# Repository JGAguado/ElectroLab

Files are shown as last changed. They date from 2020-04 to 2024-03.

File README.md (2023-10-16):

[][documentation]
[][releases]
[](LICENSE)
[][elecrow]

[][maintenance]
[][buymecoffee]

# ElectroLab

The ElectroLab board is an electronic trainer designed for educational purposes. It should be considered as a beginner-friendly guided solution for learning practical electronics where no prior knowledge is required.

With its big set of integrated components, the ElectroLab offers a very powerful and versatile platform for building up your electronic circuits in very few steps.

<p float="left">
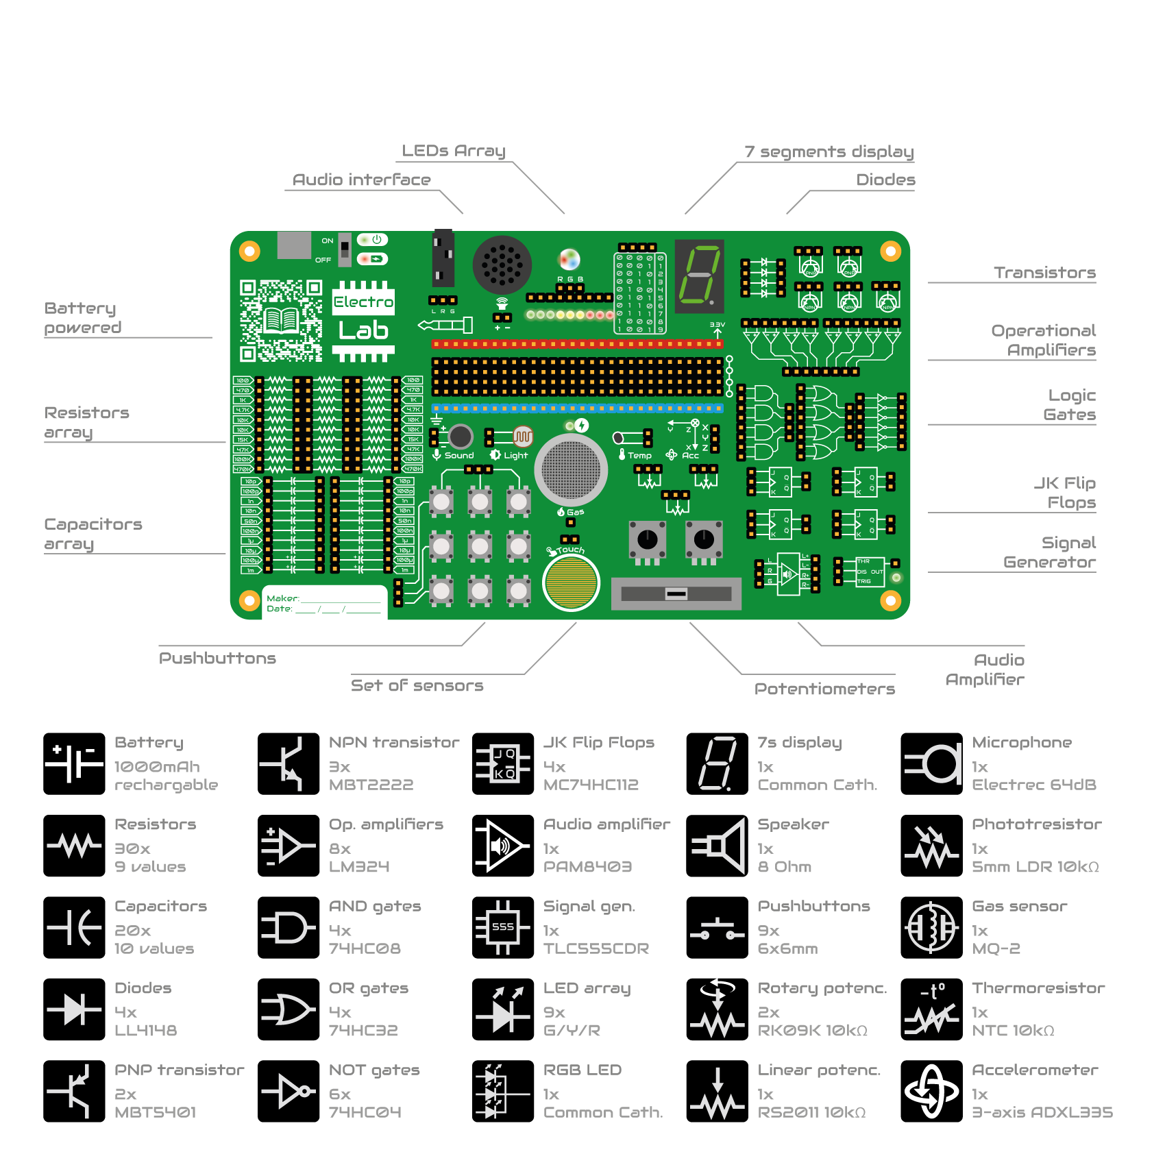
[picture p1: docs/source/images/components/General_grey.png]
   
</p>

[documentation-shield]: https://readthedocs.org/projects/electrolab/badge/?version=latest&style=for-the-badge
[documentation]: https://electrolab.readthedocs.io/en/v3/

[releases-shield]: https://img.shields.io/github/release/JGAguado/ElectroLab.svg?style=for-the-badge
[releases]: https://github.com/JGAguado/ElectroLab/releases

[license-shield]: https://img.shields.io/badge/License-CC%20BY--NC--SA%204.0-lightgrey.svg?style=for-the-badge

[maintenance-shield]: https://img.shields.io/badge/maintainer-J.%20G.%20Aguado-blue.svg?style=for-the-badge
[maintenance]: https://github.com/JGAguado

[buymecoffee-shield]: https://img.shields.io/badge/buy%20me%20a%20coffee-support-yellow.svg?style=for-the-badge
[buymecoffee]: https://www.buymeacoffee.com/J.G.Aguado

[buyit-shield]: https://img.shields.io/badge/get%20it%20on-elecrow-399BD7.svg?style=for-the-badge
[elecrow]: https://www.elecrow.com/electrolab.html

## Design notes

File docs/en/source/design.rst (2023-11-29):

📐 Design
=======================

.. _schematic:
Electronic schematics
---------------------
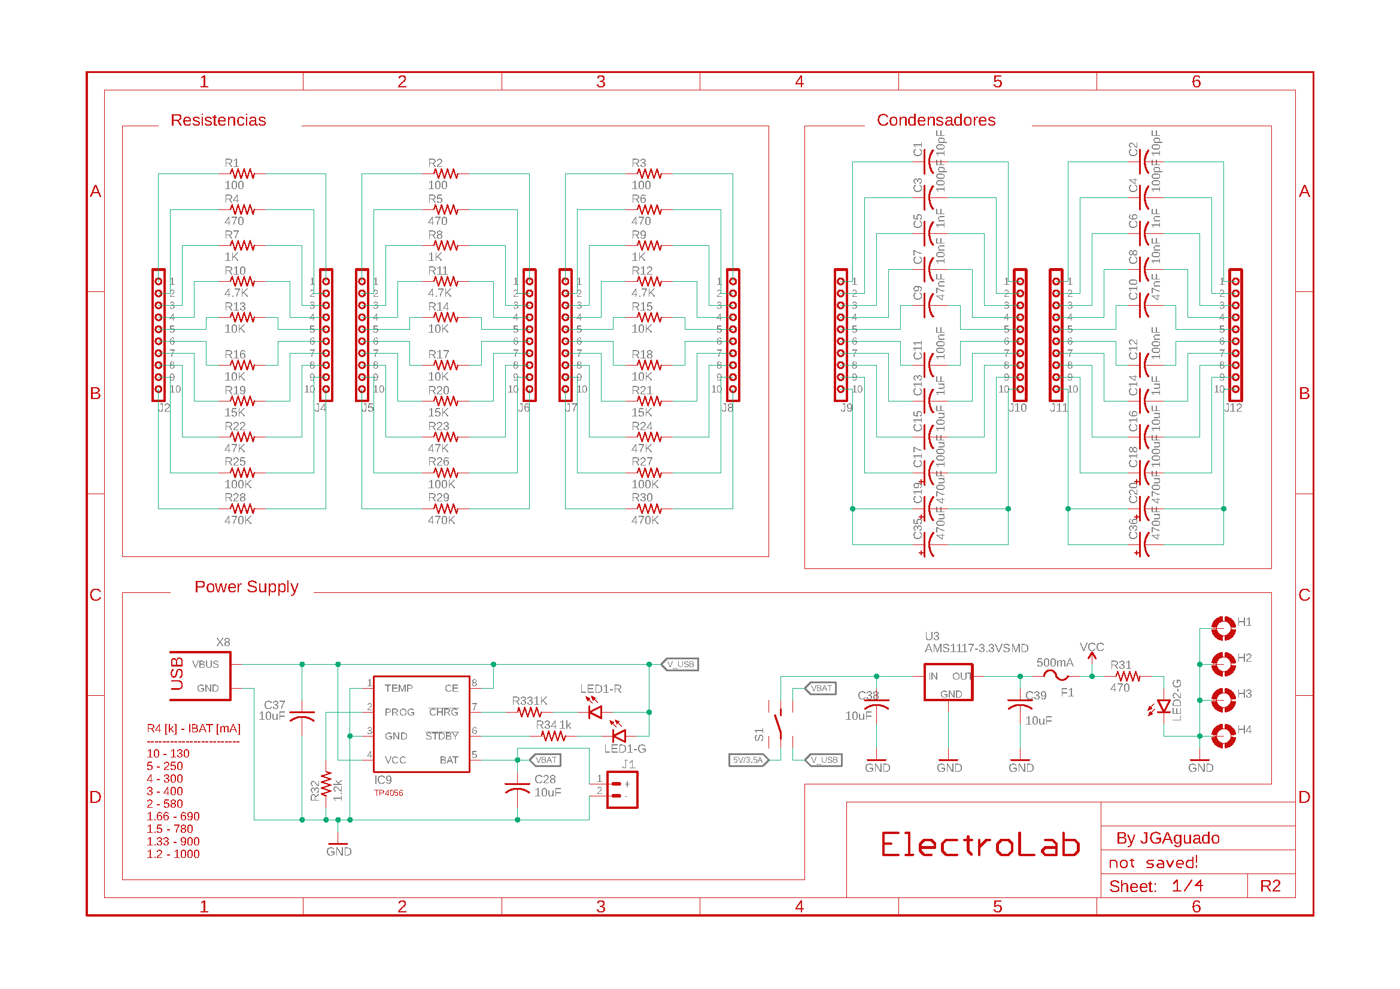
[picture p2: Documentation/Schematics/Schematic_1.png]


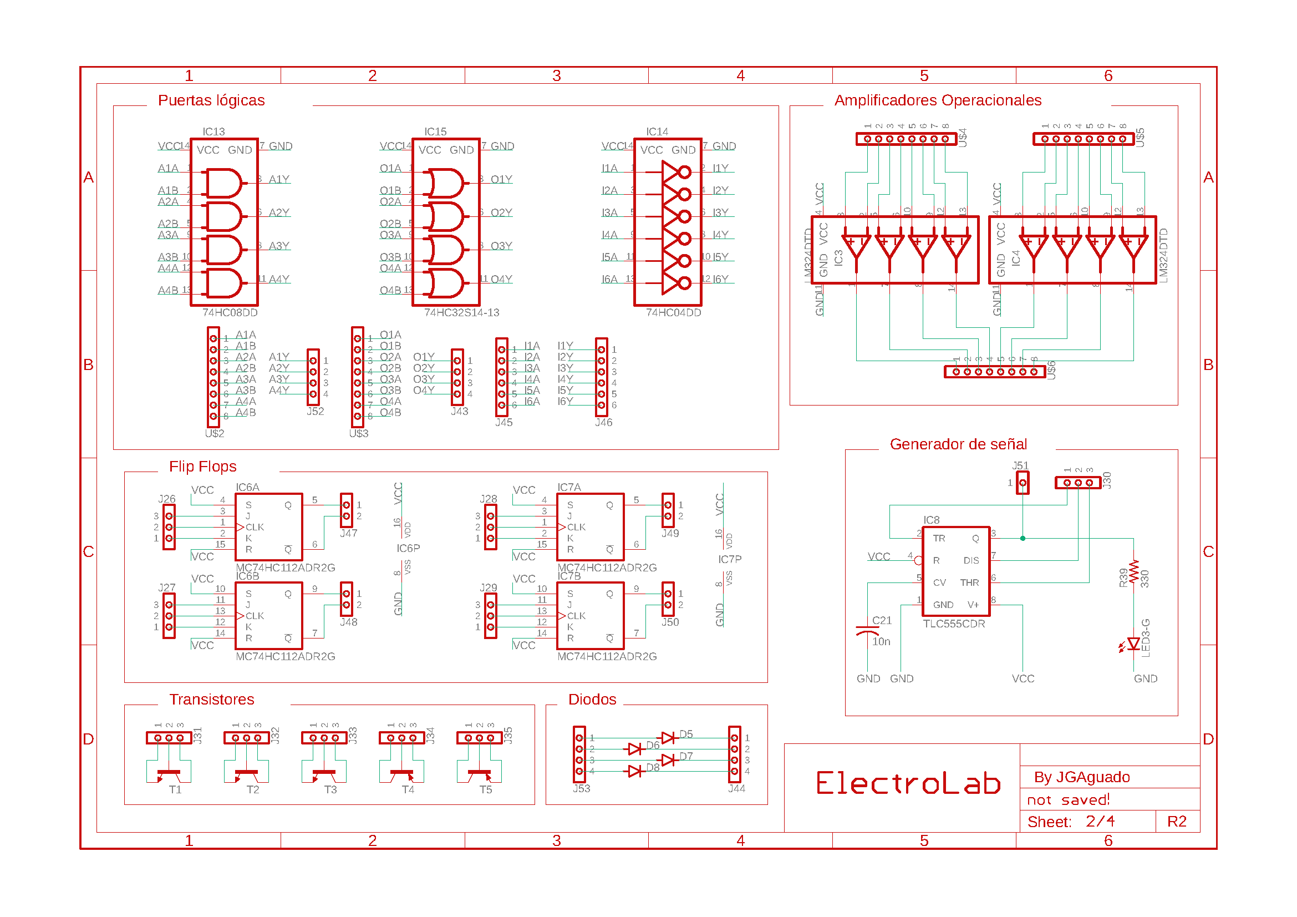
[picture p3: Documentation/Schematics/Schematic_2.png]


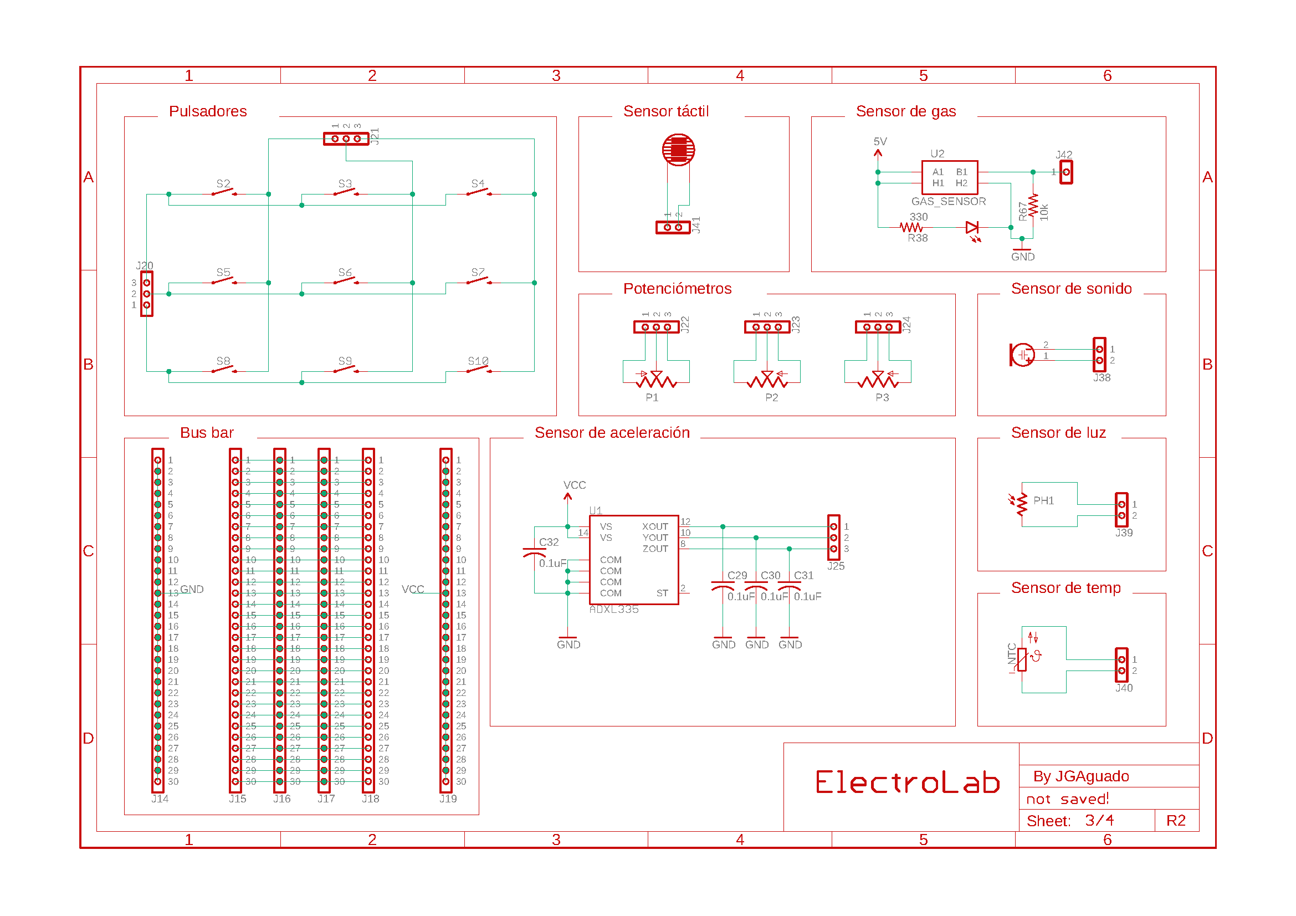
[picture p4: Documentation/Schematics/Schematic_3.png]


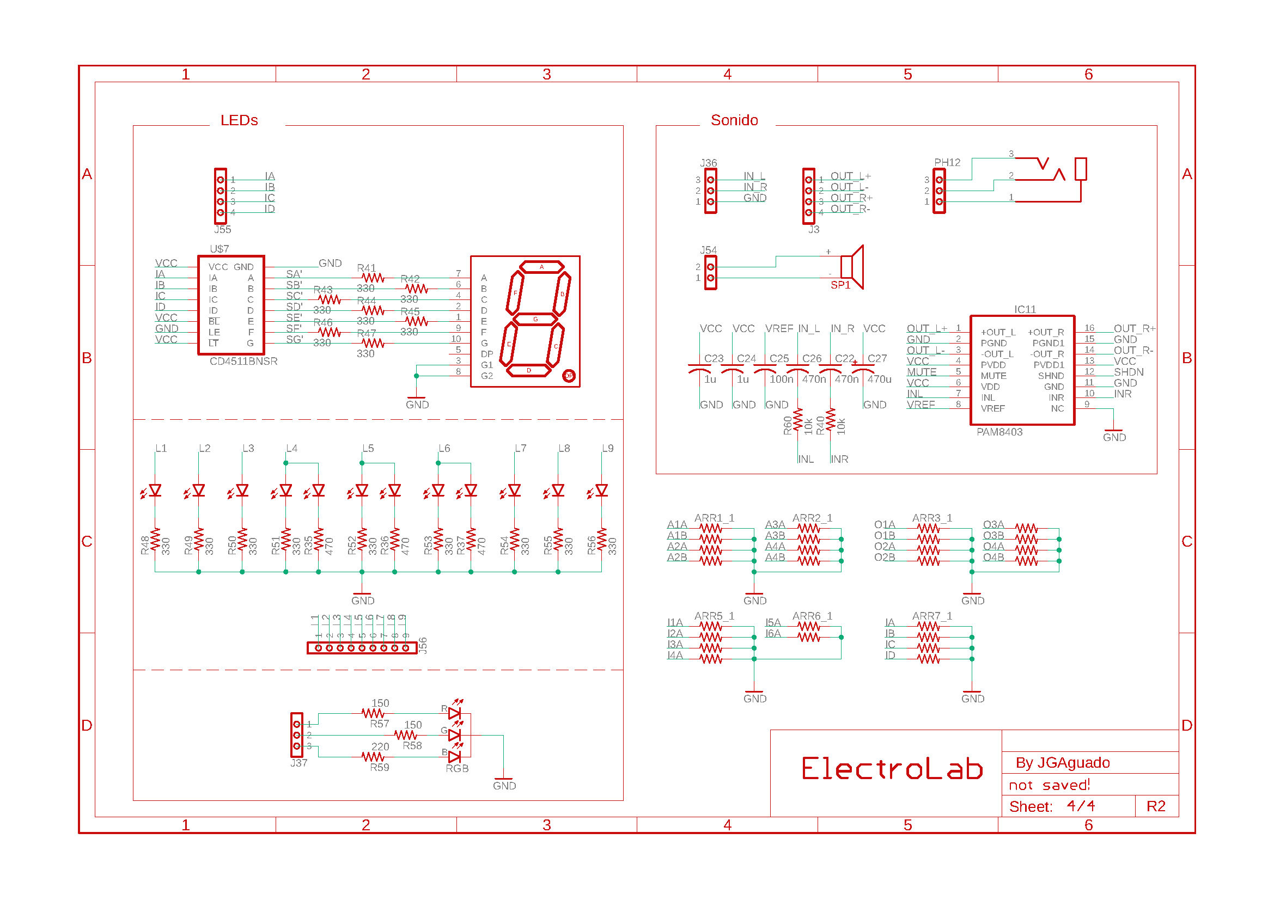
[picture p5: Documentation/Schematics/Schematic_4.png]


:download:`Download PDF <../../../Documentation/Schematics/Schematic.pdf>`

.. _pcb:

:term:`PCB`
----------

.. raw:: html

    <iframe src="_static/ibom.html" height="800px" width="100%"></iframe>

Technical Specifications
--------------------------

Electrical
^^^^^^^^^^^^

.. list-table:: 
    :widths: 50 20 20 20 20
    :header-rows: 1
    :stub-columns: 1

    * - Parameter
      - Symbol
      - Min.
      - Max.
      - Unit
    * - Supply voltage (USB)
      - :math:`V_{DC}`
      -  
      - 5
      - *V*
    * - Current consumption
      - 
      - 0.5 
      - 800
      - :math:`mA`

Environment
^^^^^^^^^^^^
.. list-table:: 
    :widths: 50 20 20 20 20 20
    :header-rows: 1
    :stub-columns: 1

    * - Parameter
      - Symbol
      - Min.
      - Typ.
      - Max.
      - Unit
    * - Working temperature [1]_
      - :math:`T_{amb}`
      - 0
      - 25 
      - 60
      - *°C*
    * - Storage temperature [1]_
      - :math:`T_{amb}`
      - 0
      - 25 
      - 60
      - *°C*

.. [1] Based on components datasheets.

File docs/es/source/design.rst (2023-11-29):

📐 Diseño
=======================

.. _schematic:
Esquemas electrónicos
---------------------








:download:`Download PDF <../../../Documentation/Schematics/Schematic.pdf>`

.. _pcb:

:term:`PCB` (Placa de Circuito Impreso)
----------

.. raw:: html

    <iframe src="_static/ibom.html" height="800px" width="100%"></iframe>

Especificaciones Técnicas
--------------------------

Eléctricas
^^^^^^^^^^^^

.. list-table:: 
    :widths: 50 20 20 20 20
    :header-rows: 1
    :stub-columns: 1

    * - Parámetro
      - Símbolo
      - Mín.
      - Máx.
      - Unidad
    * - Voltaje de alimentación (USB)
      - :math:`V_{DC}`
      -  
      - 5
      - *V*
    * - Consumo de corriente
      - 
      - 0.5 
      - 800
      - :math:`mA`

Ambientales
^^^^^^^^^^^^

.. list-table:: 
    :widths: 50 20 20 20 20 20
    :header-rows: 1
    :stub-columns: 1

    * - Parámetro
      - Símbolo
      - Mín.
      - Typ.
      - Máx.
      - Unidad
    * - Temperatura de trabajo [1]_
      - :math:`T_{amb}`
      - 0
      - 25 
      - 60
      - *°C*
    * - Temperatura de almacenamiento [1]_
      - :math:`T_{amb}`
      - 0
      - 25 
      - 60
      - *°C*

.. [1] Basado en las hojas de datos de los componentes.

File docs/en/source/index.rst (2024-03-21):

ElectroLab
###############

.. raw:: html
        
    <iframe src="_static/carousel.html" style="width: 100%; height: 300px; border: none;"></iframe>

Welcome to the documentation page of the |Product|, an electronic trainer designed for educational purposes.
It should be considered as a beginner-friendly guided solution for learning practical electronics
where no prior knowledge is required.

With its big set of integrated components, the ElectroLab offers a very powerful and versatile platform for building up your electronic circuits
in very few steps.

Contents
--------

:doc:`safety`
    How to operate and manipulate the |Product|.

:doc:`getting_started`
    First steps for starting with the |Product|.

:doc:`assembly`
    Get to know how to prepare your |Product|.

:doc:`examples`
    Example circuits ready to deploy on the |Product|.

:doc:`design`
    Design files of the |Product|.

.. _support:
Technical support
-----------------

If you have technical problems or cannot find the information that you need in the provided documentation, 
please contact me directly:

:Author: |Author|
:Contact: |Email|

:Board: |Product|
:Version: |Version|
:Date: |Date|

.. toctree::
   :maxdepth: 2
   :hidden:

   safety
   🛒 Buy <https://www.elecrow.com/electrolab.html>   
   getting_started
   assembly
   examples 
   components
   design   
   glossary
   faq

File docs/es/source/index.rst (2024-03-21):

ElectroLab
###############

.. raw:: html
        
    <iframe src="_static/carousel.html" style="width: 100%; height: 300px; border: none;"></iframe>

¡Bienvenido a la página de documentación de la |Product|!
Un intuitivo entrenador electrónico para principiantes y amantes de los circuitos.

Con su amplio conjunto de componentes integrados, la ElectroLab ofrece una plataforma muy potente y versátil para construir circuitos electrónicos
en muy pocos pasos.

Contenidos
--------

:doc:`safety`
    Cómo operar y manipular la |Product|.

:doc:`getting_started`
    Primeros pasos para comenzar con la |Product|.

:doc:`assembly`
    Aprende cómo montar tu |Product|.

:doc:`examples`
    Circuitos de ejemplo listos para implementar en |Product|.

:doc:`design`
    Archivos de diseño de la |Product|.

.. _support:
Soporte técnico
-----------------

Si tienes problemas técnicos o no puedes encontrar la información que necesitas en la documentación proporcionada, 
por favor contáctame directamente:

:Autor: |Author|
:Contacto: |Email|

:Placa: |Product|
:Versión: |Version|
:Fecha: |Date|

.. toctree::
   :maxdepth: 2
   :hidden:

   safety
   🛒 Comprar <https://www.elecrow.com/electrolab.html>      
   getting_started
   assembly
   examples 
   components
   design   
   glossary
   faq

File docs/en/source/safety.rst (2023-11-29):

🦺 Safety guidelines
=================

These safety guidelines, the operation instructions and the limit values listed in :doc:`specs` are to be read carefully before operating the product.

.. Caution::
    This product has been designed for educational applications. 
    It was not designed for any use involving serious risks or hazards that could lead to death, injury, serious physical damage, or loss of any kind without the implementation of exceptionally stringent safety precautions.

Before the operation
--------------------
Before working with the |Product|, make sure to meet all of the following criteria:

- The |Product| is placed in a stable non-conductive surface.
- There are no objects or debris stuck in between the male pins of the surface of the board.
- Do not manipulate the board if you have wet hands or in such conditions that could lead to a short-circuit.
- Do not manipulate the board if you feel that you are electrostatically charged.
- Some components have polarity, meaning that they need a specific way of being connected.Please pay attention to the (⚠️) indications in this document related to those components.

:term:`LiPo` battery powered
----------------------
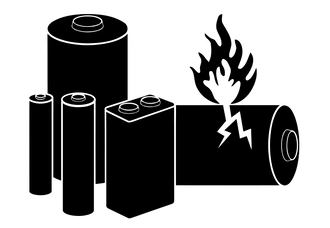
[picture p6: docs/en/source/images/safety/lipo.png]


Due to the high power density of :term:`LiPo` batteries, the |Product| is powered directly by a 1000mAh :term:`LiPo` battery. Therefore there are specific electronics embeded in charge of the battery 
management, including charge/discharge of the battery and protections against low-voltage levels and short-circuits. 

However it's not recommended to leave the product unatended while charging for long time. In case you observe a high increase of the device's temperature or you 
smell burn, immediatelly disconnect the device from the charging USB.

If you have any question, please check with :ref:`technical support <support>` before taking any action potentially dangerous.

Protection against :term:`ESD`
------------------------------

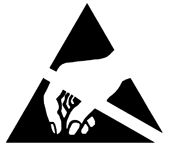
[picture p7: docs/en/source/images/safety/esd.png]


The |Product| contains components sensitive to :term:`ESD`, which can be damaged by inappropriate handling. 
It's therefore necessary to provide some safety precautions against :term:`ESD` during the handling and operation.

|
|

Usage, transport and storage
----------------------------

During the use, transport and storage, this product must be protected from any mechanical stress 
(forces applied over the board or it's components), temperatures out of the data-sheet's range, high 
environmental humidity or aggressive atmospheres.

Avoid using it in areas where it cannot be assured the previously mentioned environmental conditions.

Repairs
-------

If any of the components on the board gets damaged, a reparation is possible. This repair can be performed by 
yourself if you identify the problem and have the means for desoldering & soldering. If this is not the case,
just write to the :ref:`support <support>` mail to reach a solution.

Disposal
--------

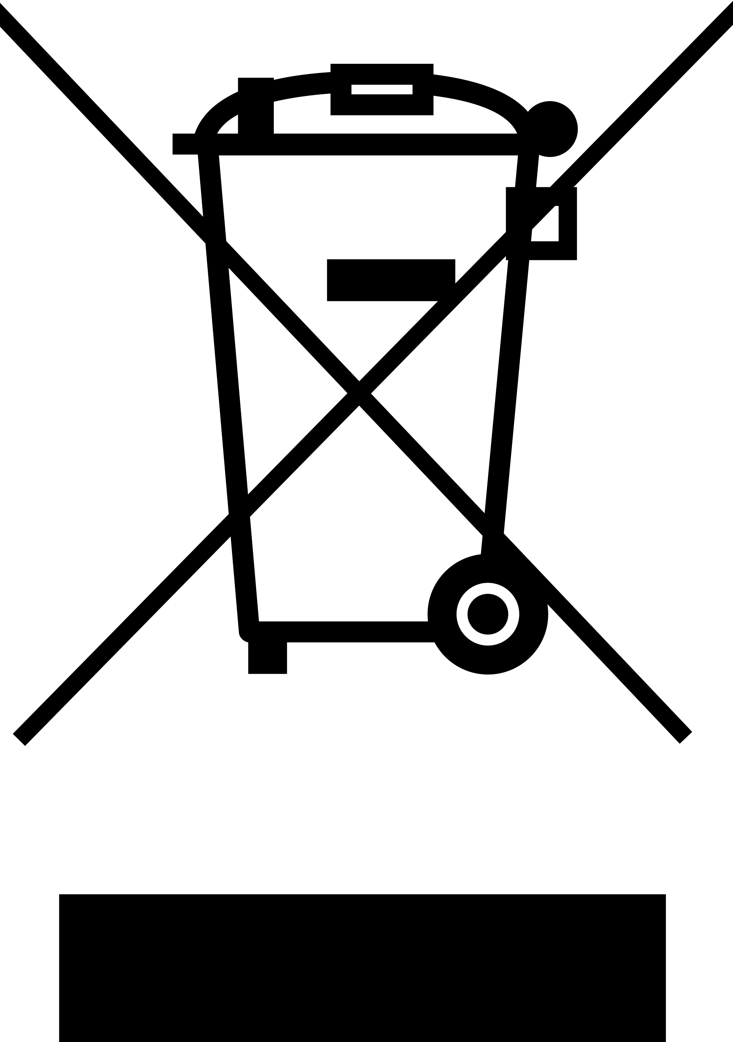
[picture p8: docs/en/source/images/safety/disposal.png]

    
In accordance with national and local environmental protection and material recovery and recycling regulations, 
electronic devices that can no longer be used (in case a repair is not possible) must be disposed of separately 
and not with normal household garbage.

|
|
|
|

Restriction of Hazardous Substances
-----------------------------------

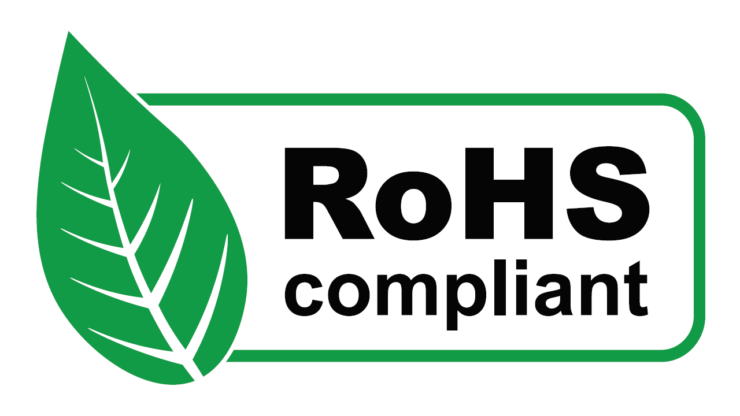
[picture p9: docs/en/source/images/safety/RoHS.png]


The :term:`PCB` and the electronic components mounted on the |Product| have been manufactured attending to the EU rules 
restricting the use of hazardous substances (:term:`RoHS`) in electrical and electronic equipment to protect the 
environment and public health.

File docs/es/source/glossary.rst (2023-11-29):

📚 Acrónimos
============

.. glossary:: 
   :sorted:

   IC
       Integrated Circuit (Circuito integrado)

   TTL
       Transistor-Transistor Logic (Logica Transistor-Transistor)

   I/O
       Inputs / Outputs (Entradas / Salidas)

   GND
       Ground (Tierra/masa)

   OTA
       Over-the-Air (remoto)

   PCB
       Printed Circuit Board (Placa de circuito impresa)

   PWM
       Pulse-width Modulation (Modulación por ancho de pulso)

   FF
       Flip Flop

   Op.Amp.
       Operational Amplifier (Amplificado operacional)

   FAQ
       Frequently Answered Questions (Preguntas frecuentemente respondidas)

   LDR
       Light Dependant Resistor (Resistencia dependiente de la luz)

   LED
       Light Emitting Diode (Diodo emisor de luz)

   LDO
       Low-dropout regulator (Regulador de baja caída de tensión)

   LiPo
       Lithium polymer battery (Batería de polímero de litio)

   RGB
       Red-Green-Blue (Rojo-Verde-Azul)

   NTC
       Negative Temperature Coefficient (Coeficiente de Temperatura Negativo)

   MDI
       Material Design Icons (Iconos de Material Design)

   MOS
       Metal Oxide Semiconductor (Semiconductor de Óxido Metálico)

   BOM
       Bill of Materials (Lista de Materiales)

   ppm
       Parts-per-million (Partes por millón)

   ESD
       Electrostatic Discharge (Descarga Electroestática)

   SMD
       Surface-mounted device (Dispositivo montado en superficie)

   SMT
       Surface-mount Technology (Tecnología de montaje superficial)

   THT
       Through Hole Technology (Tecnología de Montaje a Través de Orificios)

   IIC
       Inter-Integrated Circuit. Also known as I2C or :math:`I^2 C`. (Circuito Inter-Integrado. También conocido como I2C o :math:`I^2 C`.)

   ADC
       Analog-Digital Converter (Convertidor Analógico-Digital)

   BCD
       Binary-coded decimal (Decimal codificado en binario)

   RoHS
       Restriction of Hazardous Substances in Electrical and Electronic Equipment (Restricción de Sustancias Peligrosas en Equipos Eléctricos y Electrónicos)

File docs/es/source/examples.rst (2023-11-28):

🚀 Circuitos de ejemplo
================
Ahora que conocemos la forma de operar con el |Product|, vamos a ponernos manos a la obra.

A lo largo de los próximos documentos, verás ilustraciones interactivas como esta:

.. raw:: html
        
    <iframe src="_static/Circuits/PB_LEDs/Circuit.html" style="width: 100%; height: 500px; border: none;"></iframe>

Puedes navegar hacia adelante ➡️ y hacia atrás ⬅️ en cada paso, o ingresar directamente al paso que desees.
También puedes visualizar todos los pasos a la vez haciendo clic en el 👁 (ícono de ojo).

Siéntete libre de experimentar con los siguientes circuitos probados:

.. toctree::
   :maxdepth: 2
   :numbered:

   examples/0_basics/main
   examples/1_analog/main
   examples/2_digital/main
   examples/3_oscillators/main

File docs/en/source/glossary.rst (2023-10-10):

📚 Acronyms
============

.. glossary:: 
   :sorted:

   IC
       Integrated Circuit

   TTL
       Transistor-Transistor Logic

   I/O
       Inputs / Outputs

   GND
       Ground

   OTA
       Over-the-Air

   PCB
       Printed Circuit Board

   PWM
       Pulse-width Modulation

   FF
       Flip Flop

   Op.Amp.
       Operational Amplifier

   FAQ
       Frequently Answered Questions

   LDR
       Light Dependant Resistor

   LED
       Light Emitting Diode

   LDO
       Low-dropout regulator

   LiPo
       Lithium polymer battery

   RGB
       Red-Green-Blue

   NTC
       Negative Temperature Coefficient

   MDI
       Material Design Icons

   MOS
       Metal Oxide Semiconductor

   BOM
       Bill of Materials

   ppm
       Parts-per-million

   ESD
       Electrostatic Discharge

   SMD
       Surface-mounted device

   SMT
       Surface-mount Technology

   THT
       Through Hole Technology

   IIC
       Inter-Integrated Circuit. Also known as I2C or :math:`I^2 C`.

   ADC
       Analog-Digital Converter

   BCD
       Binary-coded decimal

   RoHS
       Restriction of Hazardous Substances (in Electrical and Electronic Equipment)

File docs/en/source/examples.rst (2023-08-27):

🚀 Example circuits
================
Now that we know the way to operate with the |Product| let's get into some real work.

Through the upcomming docs, you will see interactive illustrations like this one:

.. raw:: html
        
    <iframe src="_static/Circuits/PB_LEDs/Circuit.html" style="width: 100%; height: 500px; border: none;"></iframe>

You can navigate through each step forward ➡️ and backward ⬅️, or enter directly the step you want.
You can also visualize all the steps at once by clicking on the 👁 (eye icon).

Feel free to experiment with the following tested circuits:

.. toctree::
   :maxdepth: 2
   :numbered:

   examples/0_basics/main
   examples/1_analog/main
   examples/2_digital/main
   examples/3_oscillators/main

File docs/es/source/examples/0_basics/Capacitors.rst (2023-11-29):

Condensadores
==============

.. raw:: html
        
    <iframe src="../../_static/Circuits/Capacitors/Circuit.html" style="width: 100%; height: 500px; border: none;"></iframe>

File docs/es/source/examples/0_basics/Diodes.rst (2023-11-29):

Diodos
==============

.. raw:: html
        
    <iframe src="../../_static/Circuits/Diodes_voltage_drop/Circuit.html" style="width: 100%; height: 500px; border: none;"></iframe>

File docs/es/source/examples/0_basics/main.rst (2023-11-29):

Circuitos básicos
==============

.. toctree::
   :maxdepth: 2
   :glob:
   
   Resistors
   Capacitors
   Diodes
   Transistors

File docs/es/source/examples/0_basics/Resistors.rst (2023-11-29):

Resistencias
=================

.. raw:: html
        
    <iframe src="../../_static/Circuits/PixelRGB/Circuit.html" style="width: 100%; height: 500px; border: none;"></iframe>

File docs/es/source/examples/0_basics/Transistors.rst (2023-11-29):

Transistores
==============

.. raw:: html
        
    <iframe src="../../_static/Circuits/Tactil_amplified/Circuit.html" style="width: 100%; height: 500px; border: none;"></iframe>

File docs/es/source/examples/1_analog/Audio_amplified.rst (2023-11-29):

Amplificador de audio
==============

.. raw:: html
        
    <iframe src="../../_static/Circuits/Amplified_audio/Circuit.html" style="width: 100%; height: 500px; border: none;"></iframe>

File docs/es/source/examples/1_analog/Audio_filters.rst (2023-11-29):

Filtros de audio
==============

.. raw:: html
        
    <iframe src="../../_static/Circuits/Audio_filters/Circuit.html" style="width: 100%; height: 500px; border: none;"></iframe>

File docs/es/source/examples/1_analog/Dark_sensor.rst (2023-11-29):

Sensor de oscuridad
==============

.. raw:: html
        
    <iframe src="../../_static/Circuits/Dark_sensor/Circuit.html" style="width: 100%; height: 500px; border: none;"></iframe>

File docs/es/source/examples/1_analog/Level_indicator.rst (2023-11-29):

Indicador de nivel
===============

.. raw:: html
        
    <iframe src="../../_static/Circuits/Level_indicator/Circuit.html" style="width: 100%; height: 500px; border: none;"></iframe>

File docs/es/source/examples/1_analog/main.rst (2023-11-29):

Circuitos analógicos
==============

.. toctree::
   :maxdepth: 2
   :glob:
   
   Dark_sensor 
   Thermostat   
   Palm_detector 
   ADC 
   Audio_amplified 
   Level_indicator

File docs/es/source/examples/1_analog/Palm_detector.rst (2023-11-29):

Detector de palmadas
==============

.. raw:: html
        
    <iframe src="../../_static/Circuits/Palm_detector/Circuit.html" style="width: 100%; height: 500px; border: none;"></iframe>

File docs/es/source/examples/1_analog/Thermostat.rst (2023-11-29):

Termostato
==============

.. raw:: html
        
    <iframe src="../../_static/Circuits/Thermostat/Circuit.html" style="width: 100%; height: 500px; border: none;"></iframe>

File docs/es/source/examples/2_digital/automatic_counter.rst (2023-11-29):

Contador automático
=================

.. raw:: html
        
    <iframe src="../../_static/Circuits/Automatic_counter_0_9/Circuit.html" style="width: 100%; height: 500px; border: none;"></iframe>

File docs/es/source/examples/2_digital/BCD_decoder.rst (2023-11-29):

Decodificador :term:`BCD`
==============

.. raw:: html
        
    <iframe src="../../_static/Circuits/BCD_decoder/Circuit.html" style="width: 100%; height: 500px; border: none;"></iframe>

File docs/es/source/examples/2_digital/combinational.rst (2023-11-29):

Circuitos combinacionales
====================

.. raw:: html
        
    <iframe src="../../_static/Circuits/Combinational_circuit/Circuit.html" style="width: 100%; height: 500px; border: none;"></iframe>

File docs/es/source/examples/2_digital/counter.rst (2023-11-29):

Contador
==============

.. raw:: html
        
    <iframe src="../../_static/Circuits/Counter_0_9/Circuit.html" style="width: 100%; height: 500px; border: none;"></iframe>

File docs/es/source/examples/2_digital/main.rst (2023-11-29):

Circuitos digitales
==============

.. toctree::
   :maxdepth: 2
   :glob:
   
   BCD_decoder 
   combinational 
   palm_detector_states   
   counter 
   automatic_counter

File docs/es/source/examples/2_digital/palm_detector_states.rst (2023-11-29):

Detector de palmadas con estados
==============

.. raw:: html
        
    <iframe src="../../_static/Circuits/Palm_detector_with_states/Circuit.html" style="width: 100%; height: 500px; border: none;"></iframe>

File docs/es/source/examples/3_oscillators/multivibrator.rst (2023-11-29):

Multivibrador
==============

.. raw:: html
        
    <iframe src="../../_static/Circuits/Multivibrador_astable/Circuit.html" style="width: 100%; height: 500px; border: none;"></iframe>

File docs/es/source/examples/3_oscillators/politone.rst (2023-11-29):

Teclado politono
==============

.. raw:: html
        
    <iframe src="../../_static/Circuits/Politone_keyboard/Circuit.html" style="width: 100%; height: 500px; border: none;"></iframe>

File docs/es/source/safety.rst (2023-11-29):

🦺 Directrices de seguridad
=================

Estas directrices de seguridad, las instrucciones de operación y los valores límite enumerados en :doc:`specs` deben leerse detenidamente antes de operar el producto.

.. Caution::
    Este producto ha sido diseñado para aplicaciones educativas. 
    No fue diseñado para ningún uso que implique riesgos o peligros graves que puedan llevar a la muerte, lesiones, daños físicos graves o pérdidas de cualquier tipo sin la implementación de precauciones de seguridad excepcionalmente rigurosas.

Antes de la operación
--------------------
Antes de trabajar con la |Product|, asegúrate de cumplir con todos los siguientes criterios:

- La |Product| está colocado en una superficie estable y no conductora.
- No hay objetos o escombros atascados entre los pines macho de la superficie de la placa.
- No manipules la placa si tienes las manos mojadas o en condiciones que puedan causar un cortocircuito.
- No manipules la placa si sientes que estás cargado electrostáticamente.
- Algunos componentes tienen polaridad, lo que significa que necesitan una forma específica de ser conectados. Por favor, presta atención a las indicaciones (⚠️) en este documento relacionadas con esos componentes.

Batería :term:`LiPo`
----------------------
.. figura:: images/safety/lipo.png
    :align: right
    :figwidth: 150px

La |Product| se alimenta directamente con una batería :term:`LiPo` de 1000mAh. Por lo tanto, hay electrónica específica integrada encargada de la gestión de la batería, incluyendo la carga/descarga de la batería y protecciones contra niveles de voltaje bajo y cortocircuitos.

Sin embargo, no se recomienda dejar el producto sin supervisión mientras se carga durante mucho tiempo. En caso de observar un aumento significativo de la temperatura del dispositivo o percibir un olor a quemado, desconecta inmediatamente el dispositivo del USB de carga.

Si tienes alguna pregunta, por favor consulta con el :ref:`soporte técnico <support>` antes de tomar cualquier acción potencialmente peligrosa.

Protección contra :term:`ESD`
------------------------------

.. figura:: images/safety/esd.png
    :align: left
    :figwidth: 100px

La |Product| contiene componentes sensibles a la :term:`ESD`, que pueden dañarse por manipulación inapropiada. 
Por lo tanto, es necesario tomar algunas precauciones de seguridad contra la :term:`ESD` durante el manejo y la operación.

|
|

Uso, transporte y almacenamiento
----------------------------

Durante el uso, transporte y almacenamiento, este producto debe protegerse de cualquier estrés mecánico 
(fuerzas aplicadas sobre la placa o sus componentes), temperaturas fuera del rango indicado en la ficha técnica, alta 
humedad ambiental o atmósferas agresivas.

Evita usarla en áreas donde no se puedan asegurar las condiciones ambientales mencionadas anteriormente.

Reparaciones
-------

Si alguno de los componentes de la placa se daña, es posible realizar una reparación. Esta reparación puede ser realizada por ti mismo si identificas el problema y tienes los medios para desoldar y soldar. Si este no es el caso,
simplemente escribe al correo de :ref:`soporte <support>` para encontrar una solución.

Reciclaje
--------

.. figura:: images/safety/disposal.png
    :align: right
    :figwidth: 100px
    
De acuerdo con las regulaciones nacionales y locales de protección ambiental y recuperación y reciclaje de materiales, 
los dispositivos electrónicos que ya no se puedan usar (en caso de que no sea posible una reparación) deben ser desechados por separado 
y no con la basura doméstica normal.

|
|
|
|

Restricción de Sustancias Peligrosas
-----------------------------------

.. figura:: images/safety/RoHS.png
    :align: left
    :figwidth: 125px

El :term:`PCB` y los componentes electrónicos montados en la |Product| han sido fabricados siguiendo las normas de la UE 
que restringen el uso de sustancias peligrosas (:term:`RoHS`) en equipos eléctricos y electrónicos para proteger el 
medio ambiente y la salud pública.

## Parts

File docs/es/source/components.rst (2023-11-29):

📱 Componentes
=============

La |Product| es una placa que puede parecer compleja a primera vista debido a la densidad de componentes en el diseño. Sin embargo, una vez que te familiarizas con las diferentes partes, es bastante simple e intuitivo.

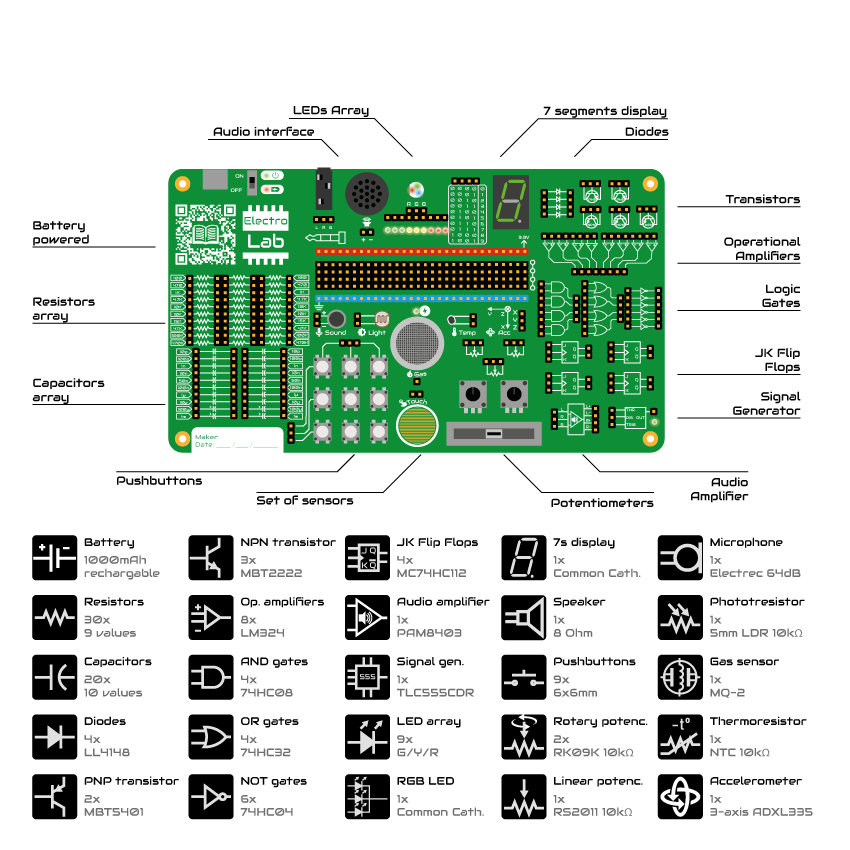
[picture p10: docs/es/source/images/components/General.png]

    
Comencemos explorando las diferentes secciones que conforman la |Product|, cómo funcionan y qué hacer con ellas.

Alimentación
-------------
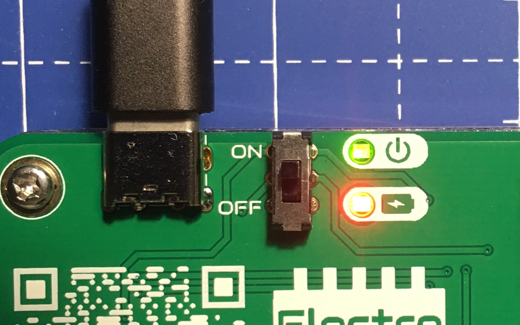
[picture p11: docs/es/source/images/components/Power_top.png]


    Vista superior

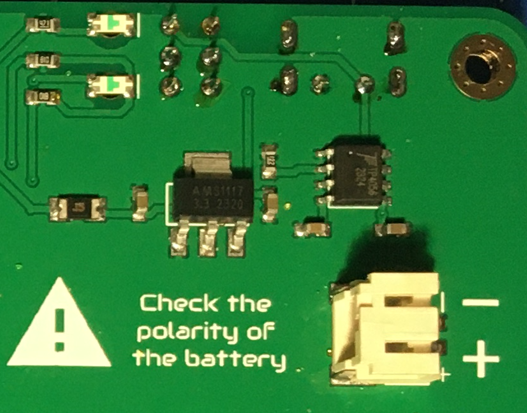
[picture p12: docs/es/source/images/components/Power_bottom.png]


    Vista inferior    

La |Product| se alimenta internamente a 3.3V (voltios). Dado que la placa funciona con batería, la forma más conveniente (y evitando conversores dc-dc) fue adaptar los 
componentes a un rango de trabajo de 3.3V.

El circuito interno para cargar la batería (que se puede consultar en el :ref:`esquema <schematic>`) está preparado para manejar los 5V nominales del puerto USB-C.

Hay un fusible rearmable y un regulador de voltaje (:term:`LDO`) después de la batería, para evitar que el resto de los componentes electrónicos reciban los 4.2V de la :term:`LiPo`.

Una vez que la placa está alimentada, no solo se energizan los Circuitos Integrados (:term:`IC`), sino que también la barra de 3.3V recibe su voltaje con respecto a la barra de :term:`GND`. La única excepción es el sensor de gas, que necesita los 5V del USB-C y solo funcionará cuando la placa esté conectada a una fuente de 5V.

La barra de 3.3V y :term:`GND` están separadas por 4 filas de otras cabeceras de clavijas. Estas cabeceras están interconectadas verticalmente, formando nodos de 4 puntos para aquellas aplicaciones que requieren múltiples conexiones en un nodo.

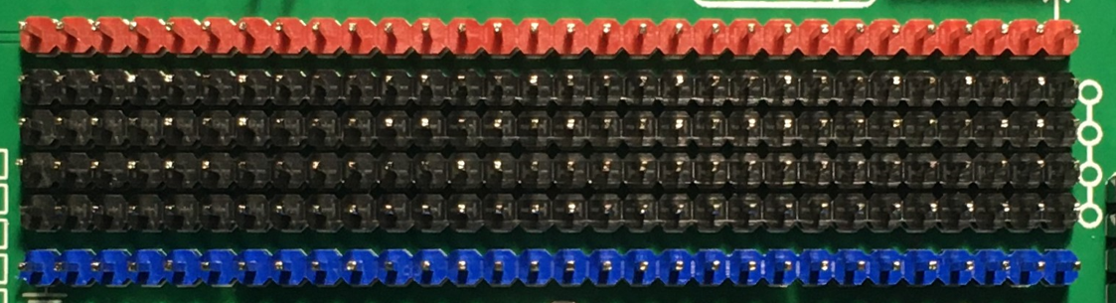
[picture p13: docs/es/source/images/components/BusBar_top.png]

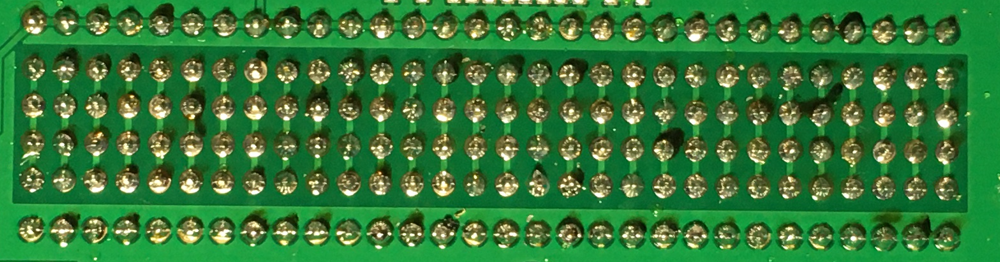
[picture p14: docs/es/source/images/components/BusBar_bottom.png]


|
|
|
|
|
|

----------

Resistencias
-------------

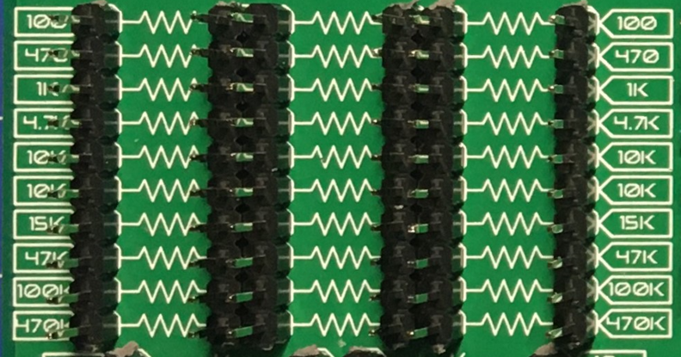
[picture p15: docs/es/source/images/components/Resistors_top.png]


    Vista superior

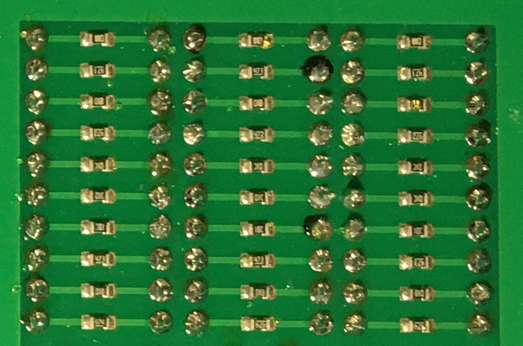
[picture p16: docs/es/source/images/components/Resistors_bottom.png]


    Vista inferior

El conjunto de resistencias, ubicado en el lado izquierdo de la |Product|, consiste en tres columnas de 10 resistencias por fila, dando un total de 30 resistencias. Como nos ha mostrado la experiencia, el valor de 10kΩ es especialmente útil (para circuitos pull-down/pull-up), por eso hay dos columnas con el mismo valor. Aparte de esta excepción, el resto de las filas tiene su propio valor individual.

Como se puede ver en la parte posterior de la placa, cada resistencia está conectada a dos cabezas de clavija macho, por lo que el acceso a cada terminal de cada resistencia es claro.

Las resistencias no tienen *polaridad*, lo que significa que cualquiera de los terminales puede ir al lado positivo o negativo de un circuito. 

Valores de resistencias:

=====  =====  ======
100Ω   100Ω   100Ω
470Ω   470Ω   470Ω
1kΩ    1kΩ    1kΩ
4.7kΩ  4.7kΩ  4.7kΩ
10kΩ   10kΩ   10kΩ
10kΩ   10kΩ   10kΩ
15kΩ   15kΩ   15kΩ
47kΩ   47kΩ   47kΩ
100kΩ  100kΩ  100kΩ
470kΩ  470kΩ  470kΩ
=====  =====  ======

----------

Condensadores 
--------------

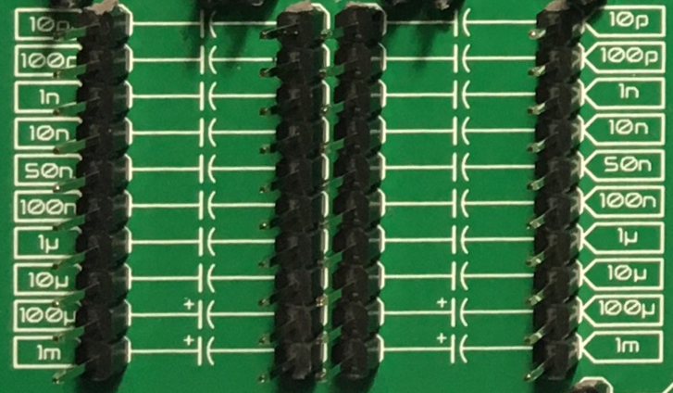
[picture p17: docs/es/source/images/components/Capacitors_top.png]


    Vista superior



    Vista inferior

El conjunto de condensadores, ubicado debajo del conjunto de resistencias, consta de dos columnas de 10 condensadores cada uno. En este caso, cada fila tiene su propio valor, dando un total de 20 condensadores, 10 valores diferentes.

Las primeras 8 filas (o valores) están formadas por condensadores cerámicos, que no tienen polaridad. Sin embargo, las dos últimas filas (valores de 100 μF y 1mF) son condensadores de tantalio, **con polaridad**.

|
|
Valores de condensadores:

=====  ===== 
10pF   10pF   
100pF  100pF   
1nF    1nΩ    
10nF   10nF  
50nF   50nF   
100nF  100nF   
1μF    1μF
10μF   10μF   
100μF  100μF  
1mF    1mF
=====  =====  

.. Caution::
     Es importante prestar atención a cómo se conectan los condensadores polarizados en el circuito **antes** de alimentarlo, asegurándose de que el lado con el símbolo **+** **nunca** vaya al :term:`GND`. 

----------

Diodos
------------



    Vista superior



    Vista inferior

La |Product| viene con un conjunto de 4 diodos, en este caso, ubicados en el lado superior derecho de la placa, entre la pantalla de 7 segmentos y los transistores.

|
|
|
|
|
|

----------

Transistores
--------------



    Vista superior



    Vista inferior

Hay dos tipos de transistores integrados en la |Product| : PNP y NPN. Ambos están ubicados en el lado superior derecho de la placa. Debido al espacio limitado en la placa y al uso más extendido del NPN, hay uno más de este tipo: 3 NPN en total y 2 de tipo PNP. 

Atendiendo a la serigrafía blanca impresa en la placa, es fácil identificar cada terminal del transistor a utilizar en el circuito.

|
|

----------

Amplificador operacional
---------------------



    Vista superior



    Vista inferior

El :term:`Op.Amp.` :term:`IC` que monta la |Product| es un LM2902DT. Cada :term:`IC` contiene hasta 4 :term:`Op.Amp.` independientes, dando un total de 8 para la placa de la |Product|, ubicados en el lado derecho de la placa.

Como se muestra en la serigrafía, las entradas al :term:`Op.Amp.` están colocadas en la parte superior, mientras que las salidas están debajo. Con un poco de zoom se puede apreciar en la serigrafía cuál entrada es la Inversora (-) y cuál es la No Inversora (+).

Como se comentó en la sección de alimentación, estos :term:`Op.Amp.` se alimentan tan pronto como se alimenta la |Product|, haciéndolos listos para ser utilizados.

|
|

----------

Puertas lógicas
-----------



    Vista superior



    Vista inferior

Pasando a los circuitos 100% digitales, la |Product| integra un conjunto de 3 compuertas lógicas diferentes: 4 AND, 4 OR y 6 NOT. El conjunto de compuertas está ubicado en el lado derecho de la placa, directamente debajo de los :term:`Op.Amp.` y dividido por columnas (según el tipo de compuerta).

Atendiendo a cada tipo de compuerta lógica, los :term:`IC` utilizados son los siguientes:

- Compuertas AND: SN74LV08ADR.
- Compuertas OR: SN74LV32ADR.
- Compuertas NOT: SN74LV04ADR.

Cuando se trabaja con niveles de 3.3V, la definición de un bit (1 o 0) se realiza mediante niveles de voltaje. Para evitar que el ruido eléctrico de fondo interfiera con nuestros procesos lógicos, todas las entradas de las compuertas lógicas se conectan a tierra a través de una matriz de resistencias de 10kΩ.

|
|

----------

Flip Flops
-----------



    Vista superior



    Vista inferior

Continuando con los circuitos digitales, y ubicado debajo de las compuertas lógicas, la |Product| integra 4 JK :term:`FF` gracias a dos :term:`IC` 4027D :term:`FF`. 

Los :term:`FF` son, al igual que en el caso de las compuertas lógicas, listos para ser utilizados.

|
|

----------

Generador de señales
-----------------



    Vista superior



    Vista inferior

La |Product| integra un generador de señal cuadrada, el conocido **555** Temporizador oscilador :term:`IC`, ubicado en la parte inferior derecha de la placa.

Este común :term:`IC` puede proporcionar señales cuadradas (0-3.3V) y dependiendo del circuito ensamblado, el 555 integrado se puede configurar como monoestable o multivibrador astable. Esto se debe a que el pin 5 del 555 :term:`IC` está internamente conectado a un condensador de 0.01μF, como se requiere para cualquier configuración monoestable o astable.

|
| 
Audio
----------------

.. Warning:: 
    El altavoz tiene polaridad. Al ensamblar este dispositivo, presta atención a las marcas debajo del sensor.



    Vista superior



    Vista inferior

Junto al generador de señales, también en la parte inferior derecha de la placa, hay un amplificador de audio de clase D basado en el :term:`IC` PAM8403.

Este amplificador estéreo de 3W sin filtro está preparado internamente para proporcionar una interfaz lista para usar, puede recibir los canales izquierdo (L) y/o derecho (R). Es importante conectar correctamente el :term:`GND` del conector al :term:`GND` del amplificador.

|
|



    Vista superior



    Vista inferior

Como parte del laboratorio de audio, hay dos componentes más: 2 conectores jack y 1 altavoz, ubicados en la parte superior de la |Product| .

|
|
|
|
----------

Optoelectrónica
----------------
.. Warning:: 
    El :term:`LED` :term:`RGB` tiene polaridad. Al ensamblar este dispositivo, asegúrate de alinear el lado plano del dispositivo con las marcas en la placa.



    Vista superior



    Vista inferior

Junto al altavoz, y continuando con las señales no eléctricas que puede emitir la |Product|, se encuentra la sección de optoelectrónica: una barra de :term:`LED` de 3 colores, un :term:`LED` :term:`RGB` y una pantalla de 7 segmentos.

La barra de luces es simplemente un conjunto de 9 :term:`LEDs` (con su resistencia correspondiente conectada internamente al ánodo) conectados a tierra. De esta manera, cuando se aplica un voltaje a cada pin del :term:`LED`, este se encenderá, tan simple como eso. La barra tiene 3 colores diferentes, verde, amarillo y rojo (de izquierda a derecha), de 3 :term:`LEDs` cada color.

El :term:`LED` :term:`RGB` es un dispositivo optoelectrónico que incluye de manera compacta 3 :term:`LEDs` diferentes de 3 colores diferentes: rojo, verde y azul (RGB). Estos 3 :term:`LEDs` están conectados por el cátodo a tierra y cada ánodo está conectado a las resistencias apropiadas, por lo que el usuario puede simplemente ingresar el voltaje individualmente: se puede replicar casi cualquier color del espectro de luz.

La pantalla de siete segmentos (7s) es el último, pero no menos importante, componente de la sección, ubicado entre el :term:`LED` :term:`RGB` y los diodos. La pantalla de 7 segmentos, nombre que recibe debido a la cantidad de *barras* que conforman cada dígito del display, está conectada internamente a un decodificador BCD :term:`IC`: el CD4511.

Este decodificador BCD a siete segmentos tiene 4 líneas de entrada y 7 líneas de salida. Esta salida se proporciona a la pantalla de 7 segmentos, a través de las resistencias requeridas, para que muestre el número decimal dependiendo de las entradas.

|
|

----------

Pulsadores
------------------



    Vista superior

Moviéndonos hacia el lado de las entradas de la placa, se pueden reconocer fácilmente los botones pulsadores en la zona inferior, junto a los condensadores.

Individualmente, un botón pulsador conecta los dos terminales que tiene si se presiona, como un interruptor, permitiendo el flujo de corriente.

En el conjunto ensamblado, cada uno de los botones pulsadores, al presionarse, conecta uno de los pines superiores con uno de los laterales, según la columna y la fila.

|
|

----------

Potenciómetros
----------------------





Un potenciómetro es una resistencia cuyos valores pueden cambiarse mediante una acción manual. En el caso de la |Product|, hay dos tipos diferentes de potenciómetros integrados: 2 rotativos y 1 lineal, ubicados en el lado inferior, junto al circuito amplificador de audio y los flip-flops.

En ambos casos, el rango de resistencia de los potenciómetros montados es de 0 a 10kΩ. Los valores mínimos se alcanzan naturalmente cuando el botón/deslizador está en la posición izquierda, y el máximo cuando están en la posición derecha.

.. Caution::
    Si estás ensamblando algún circuito no incluido en los tutoriales oficiales de la |Product|, asegúrate de que haya alguna resistencia mínima (>100Ω) en serie con el potenciómetro utilizado. Esto se recomienda porque si el potenciómetro se mueve a los valores mínimos de resistencia, la corriente que fluye a través del potenciómetro aumenta, lo que puede dañar irreversiblemente el componente.

|
|

----------

Sensores
----------------

A pesar de que ya se han presentado dos tipos de componentes de entrada, estos no pueden considerarse como sensores. Un sensor, o transductor, es un dispositivo que *convierte* un parámetro físico (como aceleración, luz o temperatura) en una señal eléctrica mensurable.

El área donde se encuentran los sensores se extiende desde el centro de la placa (debajo de la fila de pines :term:`GND`) hasta el borde inferior, formando una "T".

Micrófono
^^^^^^^^^^^^
.. Warning:: 
    Este dispositivo tiene polaridad. Al ensamblar este dispositivo, presta atención a las marcas en la placa.



    Vista superior

La |Product| incluye un pequeño micrófono que convierte señales de sonido en señales eléctricas. Este micrófono, ubicado en la parte inferior central de la placa, está diseñado para capturar sonido y convertirlo en señales eléctricas, que luego pueden ser procesadas y utilizadas por otros componentes de la |Product| .

Sensor de luz
^^^^^^^^^^^^^^
.. Warning:: 
    Este dispositivo es sensible a la luz y puede variar su comportamiento según la intensidad lumínica.



    Vista superior

La |Product| también integra un sensor de luz, conocido como un LDR (Light Dependent Resistor). Este sensor varía su resistencia dependiendo de la cantidad de luz que recibe. Ubicado junto al micrófono, en la parte inferior central de la placa, el LDR puede utilizarse para medir la intensidad de la luz en su entorno.

|
|

Termistor
^^^^^^^^^^^^^^^^^^^^^



    Vista superior

El termistor integrado en la |Product|, junto al LDR, es de tipo :term:`NTC` (Coeficiente de Temperatura Negativo). Esto significa que la resistencia disminuye a medida que aumenta la temperatura. 

Acelerómetro
^^^^^^^^^^^^^^^^^^^^^^^^^^^^^



    Vista superior



    Vista inferior

La |Product| integra un acelerómetro analógico triaxial, ubicado en el lado derecho del área de sensores. El dispositivo elegido es el transductor ADXL337 de Analog Devices, capaz de medir hasta ±3g.

El :term:`IC` del acelerómetro funciona con 3V, un regulador de voltaje está conectado internamente para proporcionar la potencia requerida al :term:`IC`. El sensor emite 3 señales, una para cada eje, desde 0 hasta 3V que corresponden al rango de -3g a +3g. Esto significa que, por ejemplo, cuando el eje Z del dispositivo está vertical (alineado con la gravedad local), los ejes X e Y del sensor deben leer 0g, proporcionando una señal de salida de ~1.5V.

|
|

Sensor de gas
^^^^^^^^^^^^^^^^^^^^^^^^^^

.. Note::
    Este sensor es el único que requiere 5VDC para funcionar. Por lo tanto, solo funcionará cuando haya una fuente de alimentación USB conectada a la placa. 
    Puedes verificar que el sensor está funcionando a través del :term:`LED` cercano al sensor.



    Vista superior



    Vista inferior

A pesar de que se pueden montar otros sensores de la serie MQ, por defecto se incluye el MQ-2. Este dispositivo es un sensor :term:`MOS`. Los sensores de óxido de metal también son conocidos como quimioresistores porque la detección se basa en el cambio de resistencia del material sensor cuando se expone a gases.

En el caso del MQ-2, el :term:`MOS` reacciona a concentraciones de GLP, humo, alcohol, propano, hidrógeno, metano y monóxido de carbono, en un rango de 200 a 10000 :term:`ppm`.

|
|

.. hint:: 
    En el caso de una lectura del sensor de 100 :term:`ppm` de CO, significaría que solo hay 100 moléculas (de 1 millón) presentes en el gas que son CO, y las otras 999900 serían de cualquier otro gas.

----------

Sensor táctil
^^^^^^^^^^^^^^^^^^^^^^^^^^^^^



    Vista superior

El sensor *táctil* se basa en la conductividad (o resistividad). Funciona midiendo la conductividad de cualquier objeto en contacto con la capa superior del sensor. El sensor está formado por 2 conjuntos de líneas horizontales interconectadas verticalmente. Si algún objeto conductor (como una gota de agua o un dedo) está en contacto con la capa, la resistencia entre los dos pines disminuye.

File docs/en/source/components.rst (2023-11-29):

📱 Components
===========
The |Product| is a board that may look complex at first sight because of the density of components in the layout. However, once you get familiarized with the different parts, it's pretty simple and intuitive.


    
Let's start by exploring the different sections that form the |Product|, how they work and what to do with them.

Power
-------------


    Top side view



    Bottom side view    

The |Product| is powered internally at 3.3V (volts). Since the board is battery powered, the most convenient way (and therefore avoiding step-up converters) was to adapt the 
components to a 3.3V working range.

The internal circuit for charging the battery (which can be consulted on the :ref:`schematic <schematic>`) is ready to handle the nominal 5V from the USB-C port.

There is a resetable fuse and a voltage regulator (:term:`LDO`) after the battery, in order to prevent the rest of the electronic components to receive the 4.2V of the :term:`LiPo`

Once the board is powered, not only the Integrated Circuits (:term:`IC`) are being energized, but also the 3.3V bar gets its voltage with respect to the :term:`GND` bar. 
The only exception is the Gas sensor, that needs the 5V from the USB-C, and that will only work when the board is wired to a 5V source.

The 3.3V & :term:`GND` bar are separated by 4 rows of other pinheads. These headers are interconnected vertically, forming nodes of 4 points for those applications that requires multiple connections in one node.




|
|
|
|
|
|

----------

Resistors
-------------



    Top side view



    Bottom side view

The resistors array, located in the left side of the |Product|, consist on three columns of 10 resistors per row, giving a total of 30 resistors. As experience has showed us, the value of 10kΩ is specially useful (for pull-down/pull-up circuits), and that is why there are two columns with the same value. Apart from this exception, the rest of rows has its own individual value.

As it can seen on the board's back, each resistor is connected to two male pinhead, so the access to each terminal of each resistor is clear.

The resistors have no *polarity*, meaning that any of the terminals can go to the positive or negative side of a circuit. 

Resistors values:

=====  =====  ======
100Ω   100Ω   100Ω
470Ω   470Ω   470Ω
1kΩ    1kΩ    1kΩ
4.7kΩ  4.7kΩ  4.7kΩ
10kΩ   10kΩ   10kΩ
10kΩ   10kΩ   10kΩ
15kΩ   15kΩ   15kΩ
47kΩ   47kΩ   47kΩ
100kΩ  100kΩ  100kΩ
470kΩ  470kΩ  470kΩ
=====  =====  ======

----------

Capacitors
--------------



    Top side view



    Bottom side view

The capacitors array, located under the resistors array, consists on two columns of 10 capacitors each. In this case each row has its own value, giving a total of 20 capacitors, 10 different values.

The first 8 rows (or values) are formed by ceramic capacitors, that have no polarity. However, the last two rows (values 100 μF and 1mF) are tantalum capacitors, **with polarity**.

|
|

Capacitors values:

=====  ===== 
10pF   10pF   
100pF  100pF   
1nF    1nΩ    
10nF   10nF  
50nF   50nF   
100nF  100nF   
1μF    1μF
10μF   10μF   
100μF  100μF  
1mF    1mF
=====  =====  

.. Warning::
     It's important to pay attention how the polarized capacitors are connected in the circuit **before** powering it, making sure that the side with the **+** symbol **never** goes to the :term:`GND`. 

----------

Diodes
------------



    Top side view



    Bottom side view

The |Product| comes with a 4 diodes set, in this case, located in the upper right side of the board, between the 7 segments display and the transistors.

|
|
|
|
|
|

----------

Transistors
--------------



    Top side view



    Bottom side view

There are two types of transistors integrated in the |Product|: PNP & NPN. Both of them are placed on the top right side of the board. Due to the limited space on the board and the more extended use of the NPN, there is one more of this type: 3 NPN in total and 2 PNP type. 

Attending to the white printed silkscreen on the board, it is easy to identify each terminal of the transistor to be used on the circuit.

|
|

----------

Operational Amplifier
---------------------



    Top side view



    Bottom side view

The :term:`Op.Amp.` :term:`IC` that the |Product| mounts is a LM2902DT. Each :term:`IC` contains up to 4 independent :term:`Op.Amp.`, giving a total of 8 for the |Product| board, located on the right side of the board.

As printed in the silkscreen, the inputs to the :term:`Op.Amp.` are placed on the upper side, while the outputs are under. With a little bit of zoom it can be appreciated in the silkscreen which input is the Inverting (-) and which one is the Non-Inverting (+)

As commented in the power section, these :term:`Op.Amp.` are powered as soon as the |Product| is powered, making them ready to be used.

|
|

----------

Logic gates
-----------



    Top side view



    Bottom side view

Moving on to the 100% digital circuits, |Product| integrates a set of 3 different logic gates: 4 AND, 4 OR and 6 NOT. The set of gates are placed on the right side of the board, directly under the :term:`Op.Amp.` and divided by columns (according to the gate type).

Attending to each type of logic gate, the used :term:`IC` are the following:

- AND gates: SN74LV08ADR. 
- OR gates: SN74LV32ADR. 
- NOT gates: SN74LV04ADR. 

When working with 3.3V levels, the definition of a bit (1 or 0) is done by voltage levels. For avoiding the background electrical noise to interfere with our logic processes, all the logic gates inputs are pulled-down through a 10kΩ resistor array.

|
|

----------

Flip Flops
-----------



    Top side view



    Bottom side view

Continuing with the digital circuits, and located under the logic gates, the |Product| integrates 4 JK :term:`FF` thanks to two 4027D :term:`IC`. 

The :term:`FF` are, like in the case of the logic gates, ready to be used. 

|
|

----------

Signal generator
-----------------



    Top side view



    Bottom side view

The |Product| integrates a square signal generator, the well-known **555** Timer oscillator :term:`IC`, placed on the bottom right side of the board.

This common :term:`IC` can provide square signals (0-3.3V) and depending on the assembled circuit the integrated 555 can be configured as monostable or astable multivibrator. This is because the pin 5 of the 555 :term:`IC` is internally connected to a 0.01μF capacitor, as it is required for any monostabe or astable configuration.

|
|

----------

Audio
----------------

.. WARNING:: 
    The speaker has polarity. When assembling this device, pay attention to the marks under the sensor.



    Top side view



    Bottom side view

Next to the signal generator, also on the bottom right side of the board, there is a class-D audio amplifier based on the PAM8403 :term:`IC`.

This filter-less 3W stereo amplifier is internally prepared to provide a ready-to-use interface, it can input the left (L) and/or right (R) channels. It is important to connect correctly the :term:`GND` from the jack to the :term:`GND` of the amplifier.

|
|



    Top side view



Bottom side view

As part of the audio laboratory there are two more components: 2 jack connectors and 1 speaker, located on the upper side of the |Product|.

|
|
|
|
----------

Opto-electronics
----------------
.. WARNING:: 
    The :term:`RGB` :term:`LED` has polarity. When assembling this device, pay attention to allign the plain side of the device 
    with the marks on the board.



    Top side view



    Bottom side view

Next to the speaker, and continuing with the non-electric signals the |Product| can output, the opto-electronics section can be found: 3-colors :term:`LED` bar, :term:`RGB` & 7 segments display.

The light bar is just a set of 9 LEDs (with their correspondent resistance internally connected to the anode) pulled to the ground. This way, when a voltage is applied to each :term:`LED` pin, this will turn on, as simple as that. The bar has 3 different colors, green, yellow and red (from left to right), of 3 LEDs each color.

The :term:`RGB` :term:`LED` is an opto-electronic device that packs in a compact way 3 different LEDs of 3 different colors: red, green and blue (RGB). These 3 LEDs are connected by the cathode to the ground and each anode of them is already connected to the appropriate resistors, so the user can just input the voltage individually: you can replicate almost any color of the light spectrum.

The seven segments (7s) :term:`LED` display is the last, but not least, component of the section, located between the :term:`RGB` :term:`LED` and the diodes. The 7 segments display, name that receives because of the amount of *bars* that conform each digit of the display, is internally connected to a BCD decoder :term:`IC`: the CD4511.

This BCD to seven segment decoder has 4 input and 7 output lines. This output is given to the 7 segment display, through the required resistors, so it displays the decimal number depending on the inputs.

|
|

----------

Push-buttons
------------------



    Top side view

Moving to the board's inputs side, we can easily recognize the push-buttons array on the bottom area next to the capacitors.

Individually, a push-button connects the two terminals it has if it is pressed, like a switch, letting the current flow. 

On the assembled array, each of the push-buttons, if pressed, connects one of the upper pins with one of the lateral pins, depending on the column and the row.

|
|

----------

Potentiometers
----------------------





A potentiometer is a resistor whose values can be changed by a manual action. In the case of the |Product|, there are two different types of integrated potentiometers: 2 rotary and 1 linear, located on the bottom side, next to the audio amplifier circuit and the flip flops.

In both cases, the resistance range the mounted potentiometers is 0 to 10kΩ. The minimum values are reached, naturally, when the knob/slider, are in the left position, and the maximum when they are in the right position.

.. Warning::
    If you are assembling any circuit non-listed in the official tutorials of the |Product|, please make sure that there is some minimum resistance (>100Ω) in series with the used potentiometer. This is recommended because if the potentiometer is moved to the minimum resistance values, the current flowing through the potentiometer increases, which can damage irreversibly the component.
 
|
|

----------

Sensors
----------------

Despite two types of input components have already been presented, these cannot be considered as sensors. A sensor, or transducer, is a device that *converts* a physical parameter (such as acceleration, light or temperature) to a measurable electrical signal.

The area where the sensors are placed extends from the center of the board (under the :term:`GND` pinhead row) to the bottom edge, forming a "T".

Microphone
^^^^^^^^^^^^
.. WARNING:: 
    This device has polarity. When assembling this device, pay attention to the marks under the sensor.



    Top side view

The electrec microphone is placed on the left side of the sensor's area. The CMEJ-0627-42-P is an omnidirectional microphone with a -42dB sensitivity.

.. Warning::
    As the electrec microphone is a component with polarity, it's important to pay attention to the **+** and **-** printed signs on the silkscreen of the |Product|

|
|

----------

LDR
^^^^^^^^^^^^



    Top side view

The :term:`LDR` is placed next to the microphone. The used component is the GL5528.

|
|
|
|
|

----------

Thermistor
^^^^^^^^^^^^



    Top side view

The thermistor component integrated in the |Product|, next to the :term:`LDR`, is a :term:`NTC` type. This means that the resistance decreases as temperature rises. 

|
|
|

----------

Accelerometer
^^^^^^^^^^^^



    Top side view



    Bottom side view

The |Product| integrates a tri-axial analog accelerometers, placed on the right side of the sensor's area. The chosen device is the ADXL337 transducer from Analog Devices, able to measure up to ±3g. 

As the accelerometer :term:`IC` works with 3V, a voltage regulator is connected internally to provide the required power to the :term:`IC`. The sensor outputs 3 signals, according to each axis, from 0 to 3V that corresponds to the range from -3g to +3g. This means that, for example, when the device's Z axis is vertical (aligned with the local gravity) the X and Y axis of the sensor should read 0g, providing an output signal of ~1.5V.

|
|

----------

Gas sensor
^^^^^^^^^^^^^^^^
.. Note::
    This sensor is the only one requiring 5VDC to work. Therefore it will only work when there is a USB powering the board. 
    You can verify this sensor is working through the :term:`LED` close to the sensor.



    Top side view



    Bottom side view

Despite you can mount any other MQ sensor series, the one by default is the MQ-2. This device is a :term:`MOS` sensor. Metal oxide sensors are also known as Chemiresistors because sensing is based on the change in resistance of the sensing material when exposed to gasses.

In the case of the MQ-2, the MOS reacts to LPG, Smoke, Alcohol, Propane, Hydrogen, Methane and Carbon Monoxide concentrations, ranging from 200 to 10000 :term:`ppm`.

|
|

.. hint:: 
    In the case of a sensor reading of 100 :term:`ppm` of CO it would mean that only 100 molecules (out of 1 million) present on the gas would be CO, and the other 999900 would be any other gas.

----------

Tactile sensor
^^^^^^^^^^^^^^^^


    Top side view

The *tactile* sensor is based on conductivity (or resistivity). It works by measuring the conductivity of any item in contact with the top's layer expoded pad. The sensor is formed by a 2 sets of horizontal lines interconnected vertically. If any conductive item (like a drop of water or a finger) is in contact with the layer, the resistance in between the two pins decreases.

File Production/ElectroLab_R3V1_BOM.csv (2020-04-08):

No. | part number/description | Package | Value | Qty | RefDefs | Note | Supplier links
1 | Resistor | 1206 | 100 Ohm | 3 | R1, R2, R3 | 5% 1/4W
2 | Resistor | 1206 | 150 Ohm | 2 | R57,R58 | 5% 1/4W
3 | Resistor | 1206 | 220 Ohm | 1 | R59 | 5% 1/4W
4 | Resistor | 1206 | 330 Ohm | 23 | R32 - R38, R41 - R56 | 5% 1/4W
5 | Resistor | 1206 | 470 Ohm | 4 | R4, R5, R6, R31 | 5% 1/4W
6 | Resistor | 1206 | 1 kOhm | 3 | R7 - R9 | 5% 1/4W
7 | Resistor | 0603 | 1 kOhm | 3 | R61 - R63 | 5% 1/4W
8 | Resistor | 0603 | 2 kOhm | 3 | R64 - R65 | 5% 1/4W
9 | Resistor | 1206 | 4,7 kOhm | 3 | R10, R11, R12 | 5% 1/4W
10 | Resistor | 1206 | 10 kOhm | 7 | R13 - R18, R60 | 5% 1/4W
11 | Resistor | 0603 | 10 kOhm | 1 | R67
12 | Resistor | 1206 | 15 kOhm | 3 | R19, R20, R21 | 5% 1/4W
13 | Resistor | 1206 | 47 kOhm | 3 | R22, R23, R24 | 5% 1/4W
14 | Resistor | 1206 | 100 kOhm | 3 | R25, R26, R27 | 5% 1/4W
15 | Resistor | 0603 | 100 kOhm | 1 | R39 | 5% 1/4W
16 | Resistor | 1206 | 470 kOhm | 3 | R28, R29, R30 | 5% 1/4W
17 | Resistor | 0603 | 1 MOhm | 1 | R40 | 5% 1/4W
18 | Bussed Resistor Array | 1206 | CAY17-102JALF | 4 | AR1 - AR4
19 | Capacitor | 1206 | 10 pF | 2 | C1, C2 | 5% 25V
20 | Capacitor | 1206 | 100 pF | 2 | C3, C4 | 5% 25V
21 | Capacitor | 1206 | 1 nF | 2 | C5, C6 | 10% 25V
22 | Capacitor | 1206 | 10 nF | 3 | C7, C8, C21 | 10% 25V
23 | Capacitor | 0603 | 10 nF | 4 | C28 - C31 | 10% 25V
24 | Capacitor | 1206 | 47 nF | 2 | C9, C10 | 20% 25V
25 | Capacitor | 1206 | 100 nF | 3 | C11, C12, C25 | 20% 25V
26 | Capacitor | 0603 | 100 nF | 2 | C22, C32 | 20% 25V
27 | Capacitor | 1206 | 470 nF | 1 | C26 | 20% 25V
28 | Capacitor | 1206 | 1 uF | 4 | C13, C14, C23, C24 | 20% 25V
29 | Capacitor | 1206 | 10 uF | 2 | C15, C16 | 20% 25V
30 | Capacitor | 0603 | 10 uF | 2 | C33, C34 | 20% 25V
31 | Tantalum Capacitor | 3216 | 100 uF | 2 | C17, C18 | 20% >10V | http://www.mouser.es/ProductDetail/Nichicon/UWX1C101MCL1GB/?qs=sGAEpiMZZMtZ1n0r9vR22RxmuzErLMSV5uXFbsNvYDE%3d
32 | Tantalum Capacitor | 7343 | 470 uF | 1 | C27 | 20% >10V | http://www.mouser.es/ProductDetail/Nichicon/UCM1A471MCL1GS/
33 | Tantalum Capacitor | 7343 | 1 mF | 2 | C19, C20 | 20% >10V | http://www.mouser.es/ProductDetail/Nichicon/UWT0J102MNL1GS/
34 | Cuadruple 2 Input Positive AND Gates | SO-14 | SN74LV08ADR | 1 | IC3 |  | http://www.mouser.es/ProductDetail/Texas-Instruments/SN74LV08ADR/?qs=sGAEpiMZZMtMa9lbYwD6ZGuuqVaqkGmOirge4NQ4WQc%3d
35 | Cuadruple 2 Input Positive OR Gates | SO-14 | SN74LV32ADR | 1 | IC4 |  | http://www.mouser.es/ProductDetail/Texas-Instruments/SN74LV32ADR/?qs=sGAEpiMZZMtMa9lbYwD6ZGuuqVaqkGmO4e9dAJI3uJI%3d
36 | Hex Inverters | SO-14 | SN74LV04ADR | 1 | IC5 |  | http://www.mouser.es/ProductDetail/Texas-Instruments/SN74LV04ADR/
37 | NPN general purpose transistor | SOT-23 | BC847C,215 | 3 | T1, T2, T3 |  | http://www.mouser.es/ProductDetail/NXP-Semiconductors/BC847C215/
38 | PNP general purpose transistor | SOT-23 | BC857C,215 | 2 | T4, T5 |  | http://www.mouser.es/ProductDetail/NXP-Semiconductors/BC857C215/
39 | Switching Chip Diode | 1206 | CD1206-S01575 | 4 | D1, D2, D3, D4 |  | http://www.mouser.es/ProductDetail/Bourns/CD1206-S01575/?qs=sGAEpiMZZMtoHjESLttvkg3793dFaTfhPYzT01eaSFU%3d
40 | Low-power quad operational amplifier | SO-14 | LM2902DT | 3 | IC1, IC2, IC12 |  | http://www.mouser.es/ProductDetail/STMicroelectronics/LM2902DT/
41 | Precision Timer | SO-8 | NE555PSR | 1 | IC8 |  | http://www.mouser.es/ProductDetail/Texas-Instruments/NE555PSR/?qs=sGAEpiMZZMuHTYi1bHPYENim6UGmH2PC
42 | Filterless 3w class-d audio amplifier | SOP-16 | PAM8403DR | 1 | IC11 |  | http://www.mouser.es/ProductDetail/Diodes-Incorporated/PAM8403DR/?qs=sGAEpiMZZMtxdzBvM0rKcW6VwckCafRVd5ssSg6lsKc%3d
43 | BCD to 7 segment decoder/driver | SO-16 | CD4511BNSR | 1 | IC10 |  | http://www.mouser.es/ProductDetail/Texas-Instruments/CD4511BNSR/?qs=sGAEpiMZZMtxONTBFIcRfsQCBiNmETR9hmp7ok3BJMM%3d
44 | One channel Toggle-mode Touch sensor IC | SOT23-6 | AT42QT1012 | 1 | IC9 |  | http://www.mouser.es/ProductDetail/Atmel/AT42QT1012-TSHR/?qs=xbJoyvfFV%2F8P3rJfwEwyNg%3D%3D
45 | Dual JK flip-flop | SO-16 | HEF4027BT,652 | 2 | IC6, IC7 |  | http://www.mouser.es/ProductDetail/NXP-Semiconductors/HEF4027BT652/
46 | Accelerometer sensor | LFCSP-16 | ADXL337 | 1 | IC13 |  | https://www.mouser.at/ProductDetail/Analog-Devices/ADXL337BCPZ-RL7?qs=sGAEpiMZZMv9Q1JI0Mo%2FtcpQQ4%2F0OMfc
47 | Voltage regulator | SOT23-5 | MIC5205 | 1 | IC14
48 | 6x6 mm Pushbutton | SMD | 2-1437565-8 | 9 | PB1 - PB9 |  | http://www.mouser.es/ProductDetail/TE-Connectivity-Alcoswitch/2-1437565-8/
49 | Sub-Miniature Slide Switches | TH | JS202011CQN | 1 | S1 |  | http://www.mouser.es/ProductDetail/CK-Components/JS202011CQN/?qs=LgMIjt8LuD%2fe%252bE3iTcEFYw%3d%3d
50 | Phone Connectors SMT 3.5MM PHONE JACK | SMD | 35RASMT4BHNTRX | 1 | JC1 |  | http://www.mouser.es/ProductDetail/Lumex/SML-LX1206IC-TR/?qs=sGAEpiMZZMseGfSY3csMkW2UPVQWgWXn0K8A2Rttmcc%3d
51 | Thermistors - NTC 1206 10Kohm 5% | 1206 | NC20K00103JBA | 1 | NTC |  | http://www.mouser.es/ProductDetail/Cree-Inc/SLV6A-FKB-CK1P1G1BB7R3R3/
52 | Standard LEDs - SMD 1206 Red | 1206 | SML-LX1206IC-TR | 3 | L14, L15, L16
53 | Standard LEDs - SMD 1206 Yellow | 1206 | SML-LX1206YW-TR | 10 | L1 - L7, L11, L12, L13
54 | Standard LEDs - SMD 1206 Green | 1206 | SML-LX1206GC-TR1 | 4 | L0, L8, L9, L10
55 | Standard LEDs - SMD RGB LED | PLCC-6 | SLV6A-FKB-CK1P1G1BB7R3R3 | 1 | RGB
56 | USB Connectors 5P MICRO USB TYPE B | SMD | 10118194-0001LF | 1 | U1
57 | Connector Header 2,54 mm 1 Pos | TH | 1p | 1 | PH1
58 | Connector Header 2,54 mm 2 Pos | TH | 1*2p 2,54 | 9 | PH2 - PH10
59 | Connector Header 2,54 mm 3 Pos | TH | 1*3p 2,54 | 20 | PH11 - PH30
60 | Connector Header 2,54 mm 4 Pos | TH | 1*4p 2,54 | 6 | PH31 - PH33, PH35 - PH37
61 | Connector Header 2,54 mm 6 Pos | TH | 1*6p 2,54 | 3 | PH38, PH39, PH40
62 | Connector Header 2,54 mm 14 Pos (2x7) | TH | 2*7p 2,54 | 1 | PH41
63 | Connector Header 2,54 mm 8 Pos | TH | 1*8p 2,54 | 5 | PH42 - PH46
64 | Connector Header 2,54 mm 9 Pos | TH | 1*9p 2,54 | 1 | PH47
65 | Connector Header 2,54 mm 10 Pos | TH | 1*10p 2,54 | 10 | PH48 - PH57
66 | Connector Header 2,54 mm 30 Pos | TH | 1*30p 2,54 | 5 | PH58 - PH62
67 | Connector Header 2,54 mm 16 Pos (2x8) | TH | 2*8p 2,54 | 1 | PH63 |  | https://www.digikey.com/products/en?keywords=SBH11-PBPC-D08-RA-BK
68 | Photocell | TH | GL5528 | 1 | LDR | SBH11-PBPC-D08-RA-BK
69 | 2x7 segments display | TH | LTD-4708JR | 1 | DP1 | Common cathode 2x7 | https://www.mouser.at/ProductDetail/Lite-On/LTD-4708JR
70 | Electrec Microphone | TH |  | 1 | MIC | CMEJ-0627-42-P | https://www.mouser.at/ProductDetail/CUI-Devices/CMEJ-0627-42-P
71 | Sliding potentiometer | TH | PTA2043-2015CPB103 | 1 | P1 |  | https://www.mouser.at/ProductDetail/Bourns/PTA2043-2015CPB103
72 | Rotary potentiometer | TH | RK09K1130081 | 2 | P2, P3 |  | https://www.mouser.at/ProductDetail/ALPS/RK09K1130081
73 | Speaker | TH | AST-01708MR-R | 1 | SP1 |  | https://www.mouser.at/ProductDetail/PUI-Audio/AST-01708MR-R

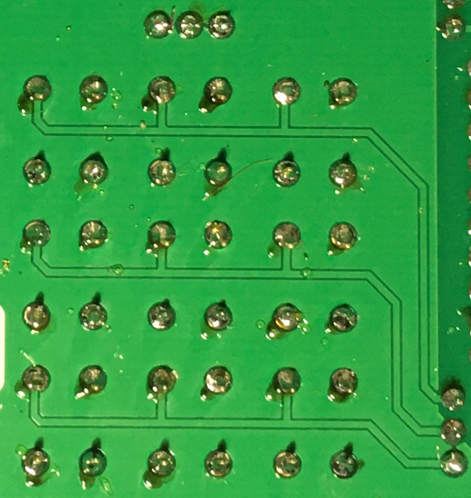
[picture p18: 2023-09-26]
docs/en/source/images/components/Pushbuttons_bottom.png

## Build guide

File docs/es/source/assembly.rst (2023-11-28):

🛠 Montaje 
===========

    .. imagen:: images/assembly/CQN23016K_kits_02.png
        :width: 40%
        :align: left
        :alt: Contenido del kit

la |Product| se puede pedir parcialmente ensamblada, donde todos los componentes :term:`SMD` ya están ensamblados y solo necesitas montar y soldar los componentes :term:`THT`, como los pines y el resto de los componentes en la cara superior.

.. Caution::
    Si nunca antes has soldado ningún componente electrónico, este kit puede resultarte bastante complicado y, por lo tanto, se recomienda encarecidamente hacerlo acompañado por alguien con algo de experiencia.

.. Note::
    Ensamblar todos los componentes :term:`THT` puede llevar algo de tiempo (1-2 horas) ya que hay más de 500 puntos de soldadura.

Herramientas
-----
.. Tip:: 
    Invertir en herramientas de calidad asegurará una experiencia de soldadura electrónica más suave y precisa, y a largo plazo merece la pena.

1. Soldador / Estación de soldadura:
    :Rango de precios: 15€ a 50€ por un soldador, 50€ a 150€ por una estación
    Esencial para unir componentes electrónicos. Un soldador en el rango de 25-60 vatios y 
    con un rango de temperatura de alrededor de 300°C a 400°C debería cubrir la mayoría de las tareas de soldadura electrónica. 
    
    En cuanto a la punta, generalmente se recomienda una punta cónica fina o plana para el trabajo electrónico, ya que proporciona precisión y control.    
    El tamaño de la punta puede variar, pero una punta con un ancho de alrededor de 1 mm suele ser un buen punto de partida para la mayoría de los proyectos. 
    Algunas estaciones de soldadura ofrecen puntas intercambiables, lo que te permite seleccionar la más adecuada para tu tarea.

    .. imagen:: images/assembly/VTSSC40N.png
        :width: 60%
        :align: center
        :alt: VTSSC40N

2. Hilo de soldadura:
    :Rango de precios: 5€ a 15€ (bobina de 100g)
    Material utilizado para crear conexiones eléctricas. 
    Los diámetros comunes para trabajos electrónicos incluyen 0.8 mm (0.031"), 1.0 mm (0.039") y 1.2 mm (0.047"). 
    La soldadura más delgada (por ejemplo, 0.8 mm) es adecuada para trabajos finos y delicados, como la soldadura de la **ElectroLab**, 
    mientras que la soldadura más gruesa (por ejemplo, 1.2 mm) se puede usar para componentes y cables más grandes.

    .. imagen:: images/assembly/solder-wire.png
        :width: 60%
        :align: center

    Hay dos tipos principales de soldadura: con plomo y sin plomo. Cada uno tiene sus propias consideraciones:

    - Soldadura con plomo (por ejemplo, 60/40 o 63/37):

        - La soldadura con plomo contiene un pequeño porcentaje de plomo, que puede proporcionar uniones de soldadura más suaves y un flujo más fácil.
        - Tiene un punto de fusión más bajo (normalmente alrededor de 183°C o 361°F), lo que facilita su manipulación.
        - **Asegúrate de tener ventilación adecuada** o usa un extractor de humos al usar soldadura con plomo para evitar inhalar los humos.
        - **Lávate las manos** a fondo después de manipular soldadura con plomo y componentes.

    - Soldadura sin plomo:

        - La soldadura sin plomo es respetuosa con el medio ambiente y cumple con las regulaciones :term:`RoHS`.
        - Tiene un punto de fusión más alto (normalmente alrededor de 217°C o 422°F) en comparación con la soldadura con plomo, por lo que es posible que debas ajustar la temperatura de tu soldador en consecuencia.
        - La soldadura sin plomo puede requerir técnicas ligeramente diferentes, como mantener la punta del soldador en la unión durante un tiempo ligeramente más largo.
        - Generalmente se considera más segura en términos de impacto en la salud y el medio ambiente, pero puede ser menos indulgente para principiantes debido a su punto de fusión más alto.

3. Alicates de corte:
    :Rango de precios: 5€ a 20€
    Utilizados para recortar los excesos de pines y cables después de la soldadura. 
    Busca filos afilados y puntas de precisión, mangos ergonómicos y materiales resistentes a la corrosión.

    .. imagen:: images/assembly/Pliers.png
        :width: 60%
        :align: center

4. Soporte PCBs:
    :Rango de precios: 10€ a 30€
    Aunque esto es más una elección personal y no una herramienta requerida, un buen soporte de PCBs asegurará tu placa durante la soldadura y te ayudará en el ensamblaje. 
    Elige uno con presión de sujeción ajustable, una superficie que no deje marcas y un mecanismo de sujeción estable.

    .. imagen:: images/assembly/Clamp.png
        :width: 60%
        :align: center

.. admonition:: Y, por cierto...

    Para facilitar el ensamblaje de los componentes :term:`THT`, la |Product| viene con una placa *Stencil* que 
    te ayudará con la posición de los pines para soldar. 

    .. imagen:: images/assembly/Top_stencil.png
        :width: 49%

    .. imagen:: images/assembly/Bottom_stencil.png
        :width: 49%

Pasos
-----

1. Coloca 2 tornillos en la |Product| en diagonal, con la cabeza del tornillo viniendo desde la parte inferior (la que tiene los componentes :term:`SMD`) y agrega una tuerca en la parte superior de la placa (la que tiene el código QR).

    .. imagen:: images/assembly/1.PNG
        :width: 60%
        :align: center

2. Comienza con los pines. Coloca **todos** los pines en la cara superior de la |Product|. Asegúrate de introducir el lado corto de los pines en la :term:`PCB`.

    .. imagen:: images/assembly/2.PNG
        :width: 60%
        :align: center

3. Una vez que hayas colocado todos los pines, coloca suavemente la placa *Stencil* sobre estos. Ten paciencia, algunos (como el del generador de señales o el sensor de gas) pueden volverse rebeldes y difíciles. Una vez que todos estén en su lugar, atornilla otras 2 tuercas a los tornillos para asegurar las dos placas juntas.

    .. imagen:: images/assembly/3.PNG
        :width: 49%

    .. imagen:: images/assembly/4.PNG
        :width: 49%

4. Con los pines correctamente asegurados, procede a soldarlos individualmente en el **reverso de la ElectroLab**. Presta especial atención a esas soldaduras cerca de los componentes :term:`SMD` para evitar cualquier daño.

    .. imagen:: images/assembly/6.gif
        :width: 60%
        :align: center
        
5. Después de soldar todos los pines, quita los tornillos y separa las placas.

    .. imagen:: images/assembly/8.PNG
        :width: 60%
        :align: center
        
6. Continúa con cada componente :term:`THT` individual, comenzando por los más pequeños como los interruptores y sensores. En este caso, se recomienda:

    .. WARNING:: 
        Algunos componentes tienen **polaridad**, lo que significa que deben ensamblarse de una manera específica, presta atención a las marcas debajo del sensor.
        Esos componentes :term:`THT` son el altavoz, el micrófono, el :term:`LED` :term:`RGB` y el display de 7 segmentos.

    1. Coloca el componente en la cara superior de la placa.

        .. imagen:: images/assembly/9.PNG
            :width: 60%
            :align: center

    2. Si tiene patitas largas que puedan doblarse (como el sensor :term:`LDR`), dóblalas para mantener el componente en su lugar. 
    Si no, presiónalo para mantenerlo en posición mientras sueldas (como el altavoz).

    3. Comienza soldando solo uno de las patitas. 
            
        .. imagen:: images/assembly/10.PNG
            :width: 60%
            :align: center

    4. Verifica si el sensor todavía está en la posición correcta y corrígelo si es necesario.
    5. Suelda el resto de las patitas de los componentes y corta la longitud sobrante de estos.
            
        .. imagen:: images/assembly/13.gif
            :width: 60%
            :align: center

    .. Attention:: 
        Por favor, ten cuidado al recortar el metal sobrante de las patas de los componentes.  
        Se recomienda usar gafas de seguridad mientras realizas esta tarea para evitar posibles lesiones oculares.

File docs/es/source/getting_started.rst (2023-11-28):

💡 Empezando
===============

.. figura:: images/getting_started/Multivibrator.gif
    :align: right
    :figwidth: 500px

    Circuito oscilador

La placa ElectroLab se vende como un kit, lo que significa que tendrás que ensamblarla (y soldarla). Lo primero que debes hacer 
una vez que recibas tu kit es asegurarte de encontrar todos los componentes incluidos:

1. Placa ElectroLab (PCB verde)
2. Placa de estarcido (PCB morado)
3. Cables duPont hembra-hembra (paquete de 40)
4. Componentes THT:

    - 2x Potenciómetros rotativos
    - 1x Potenciómetro lineal
    - 1x Altavoz
    - 1x Display de 7 segmentos
    - 1x LED RGB
    - 1x Interruptor deslizante
    - 1x Conector USB-C
    - 1x Termistor NTC
    - 1x Fotoresistor LDR
    - 1x Micrófono
    - 9x Botón pulsador
    - 1x Conector jack de 3.5 mm
    - 1x Sensor de gas MQ-2
    - 1x Pines macho azules
    - 1x Pines macho rojo
    - 10x Pines macho negro

y opcionalmente podrías haber adquirido:

- Una batería LiPo de 1000mAh
- Un protector que consiste en:

    - 3 placas acrílicas transparentes
    - Conjunto de 4 tornillos (tornillo, arandela y tuerca)

Después de ensamblarlo (visita la sección de :doc:`assembly`), podrás hacer tus propios circuitos o comenzar a explorar los que se encuentran en la sección de :doc:`examples`.

🎓¿Cómo funciona?
-------------
En el |Product|, cada componente está alimentado internamente y sus :term:`I/O` ya están conectadas a un cabezal de pin accesible. Esto facilita mucho la creación rápida de circuitos electrónicos, ya que solo necesitas interconectarlos con cables hembra-hembra.

Mientras trabajas con el |Product|, asegúrate de seguir estos pasos:

- ✅ Analiza y comprende el esquemático que deseas ensamblar con el |Product|.

- ✅ Verifica si usarás componentes polarizados (como los condensadores polarizados o el micrófono) para prestar atención adicional.

- ✅ Antes de enchufar o desenchufar cualquier cable puente, asegúrate de que la placa esté apagada:

- ✅ Ensambla el circuito siguiendo un orden conocido, te ahorrará tiempo en caso de que te pierdas.

- ✅ Comprueba que no haya ningún cable conectando 3.3V a :term:`GND`.

- ✅ Conecta el cable USB o la Interfaz Auxiliar para alimentar la placa.

- ✅ Cambia el interruptor y verifica que el LED de encendido se encienda.

- ✅ ¡Juega con tu circuito recién ensamblado y experimenta con seguridad!

.. Caution::
    Si el indicador LED de encendido no se enciende, apaga la placa y verifica el circuito: ¡puede que tengas un cortocircuito en algún lugar!

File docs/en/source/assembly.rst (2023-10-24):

🛠 Assembly 
===========

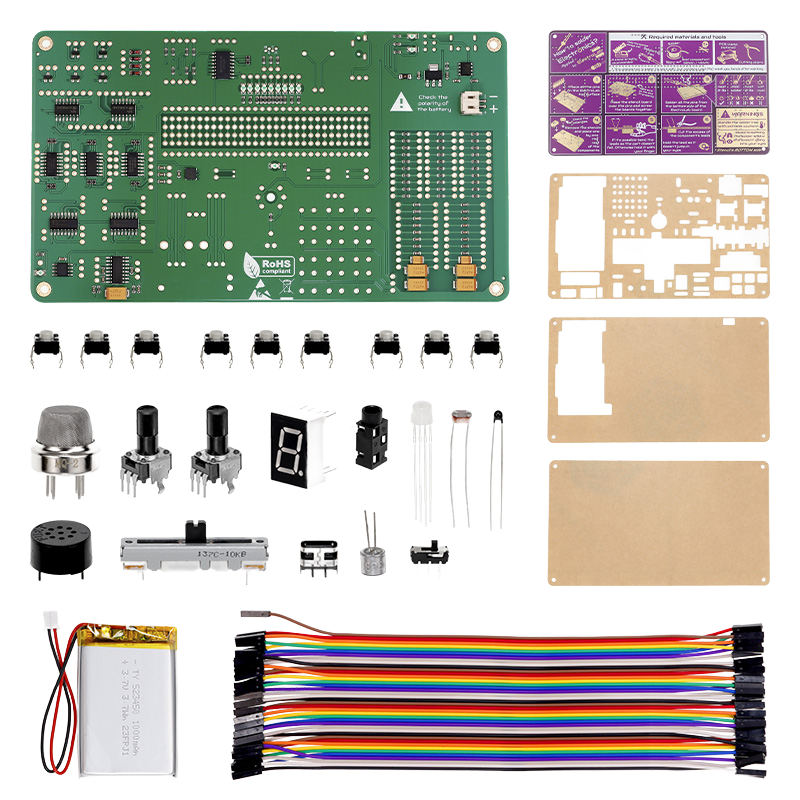
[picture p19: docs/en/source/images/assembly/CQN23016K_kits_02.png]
Kit contain
    
        
The |Product| can be ordered partially assembled, where all the :term:`SMD`
components are already assembled and you only need to assemble and solder the :term:`THT`
components, such as the pinheads and the rest of the components on the top side.

.. Caution::
    If you have never soldered any electronic component before, this kit may result quite challenging for you and therefore is highly 
    recommended to do it accompanied by someone with some experience.

.. Note::
    Assembling all the :term:`THT` components can take some time (1-2h) since there are more than 500 soldering points.

Tools
-----
.. Tip:: 
    Investing in quality tools will ensure a smoother and more precise soldering and electronics assembly experience, making your projects more efficient and successful in the long run.

1. Soldering Iron/Soldering Station:
    :Price range: $15 to $50 for a soldering iron, $50 to $150 for a station
    Essential for joining electronic components. A soldering iron in the range of 25-60 watts and 
    with a temperature range of around 300°C to 400°C (572°F to 752°F) should cover most electronics soldering tasks. 
    
    Regarding the tip, a fine conical or chisel tip is generally recommended for electronics work, as it provides precision and control.    
    Tip size can vary, but a tip with a width of around 1mm is often a good starting point for most projects. 
    Some soldering stations offer interchangeable tips, allowing you to select the most suitable one for your task. 

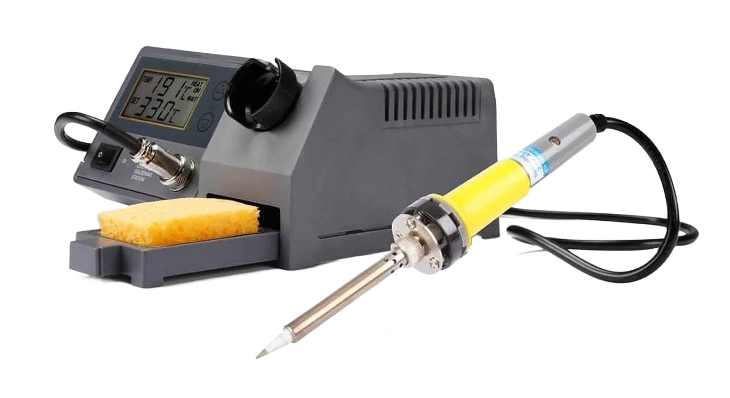
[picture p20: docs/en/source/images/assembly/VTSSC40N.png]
VTSSC40N
    

2. Solder Wire:
    :Price range: $5 to $15 (100g spool)
    Material used to create electrical connections. 
    Common diameters for electronics work include 0.8mm (0.031"), 1.0mm (0.039"), and 1.2mm (0.047"). 
    Thinner solder (e.g., 0.8mm) is suitable for fine, delicate work, like the **ElectroLab** soldering, 
    while thicker solder (e.g., 1.2mm) can be used for larger components and wires.

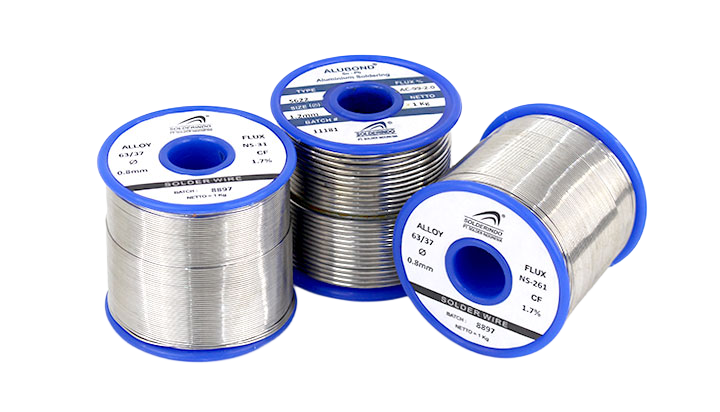
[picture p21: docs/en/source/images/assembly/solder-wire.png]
    

    There are two main types of solder: leaded and lead-free. Each has its own considerations:

    - Leaded Solder (e.g., 60/40 or 63/37):

        - Leaded solder contains a small percentage of lead, which can provide smoother solder joints and easier flow.
        - It has a lower melting point (typically around 183°C or 361°F), making it easier to work with.
        - **Ensure proper ventilation** or use a fume extractor when using leaded solder to avoid inhaling lead fumes.
        - **Wash your hands** thoroughly after handling leaded solder and components.

    - Lead-Free Solder:

        - Lead-free solder is environmentally friendly and complies with :term:`RoHS` regulations.
        - It has a higher melting point (typically around 217°C or 422°F) compared to leaded solder, so you may need to adjust your soldering iron's temperature settings accordingly.
        - Lead-free solder may require slightly different techniques, such as holding the soldering iron tip on the joint for a slightly longer time.
        - It's generally considered safer in terms of health and environmental impact but can be less forgiving for beginners due to its higher melting point.

3. Cutting Pliers:
    :Price range: $5 to $20
    Used for trimming excess leads and wires after soldering. 
    Look for sharp, precision-ground jaws, ergonomic handles, and corrosion-resistant materials.

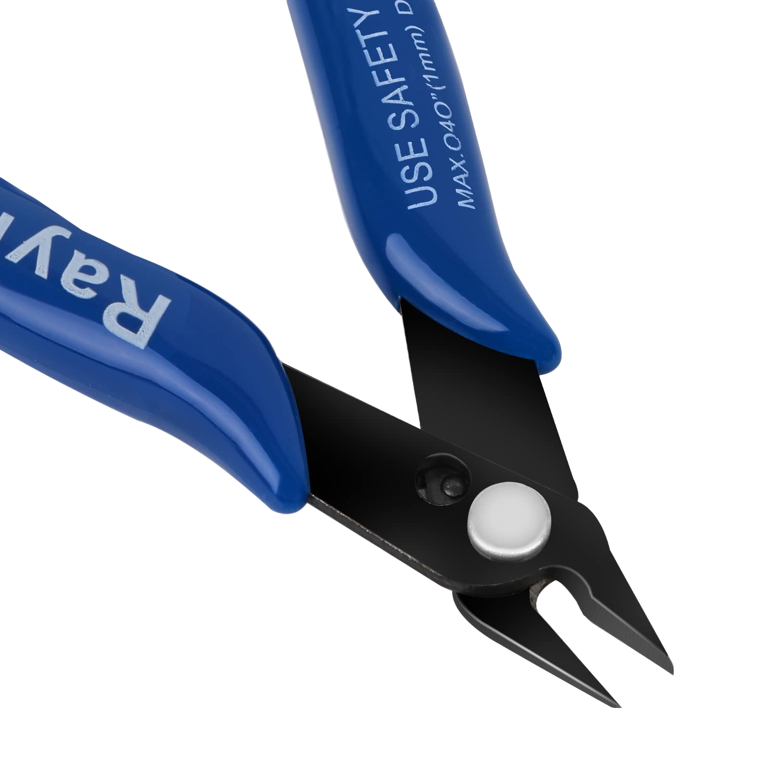
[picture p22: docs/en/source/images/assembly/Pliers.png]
    

4. PCB Clamp:
    :Price range: $10 to $30
    Althoug this is more of a personal choice and not a required tool, a good PCB clamp will secure your board during soldering and help you on the assembly. 
    Choose one with adjustable clamping pressure, a non-marring surface, and a stable base or attachment mechanism.

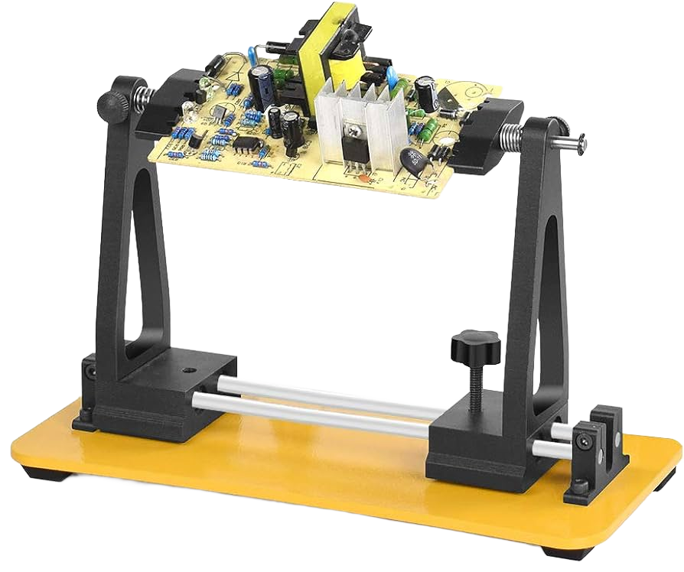
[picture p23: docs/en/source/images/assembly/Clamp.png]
    

.. admonition:: And, by the way...

    For making easier the :term:`THT` components assembly, the |Product| comes with a *Stencil board* that will 
    help you with the pinheads positioning for soldering. 

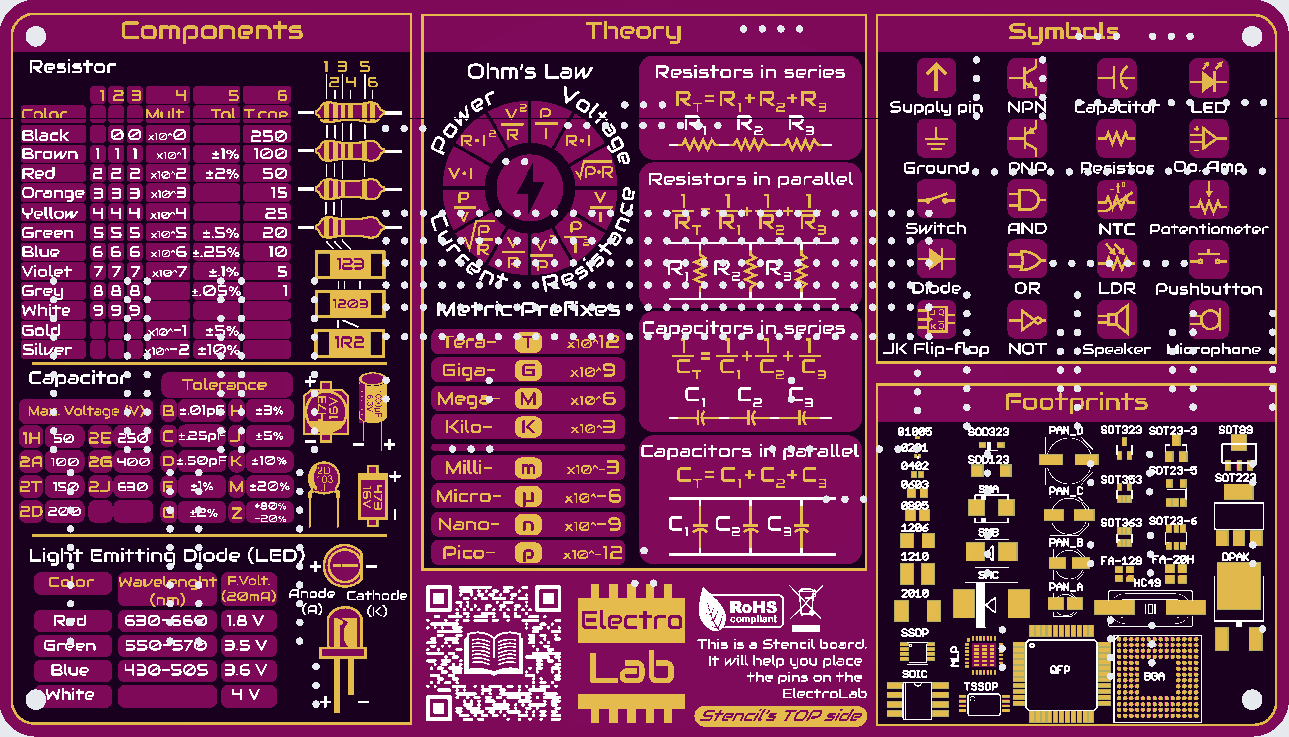
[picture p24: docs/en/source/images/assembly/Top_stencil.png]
    

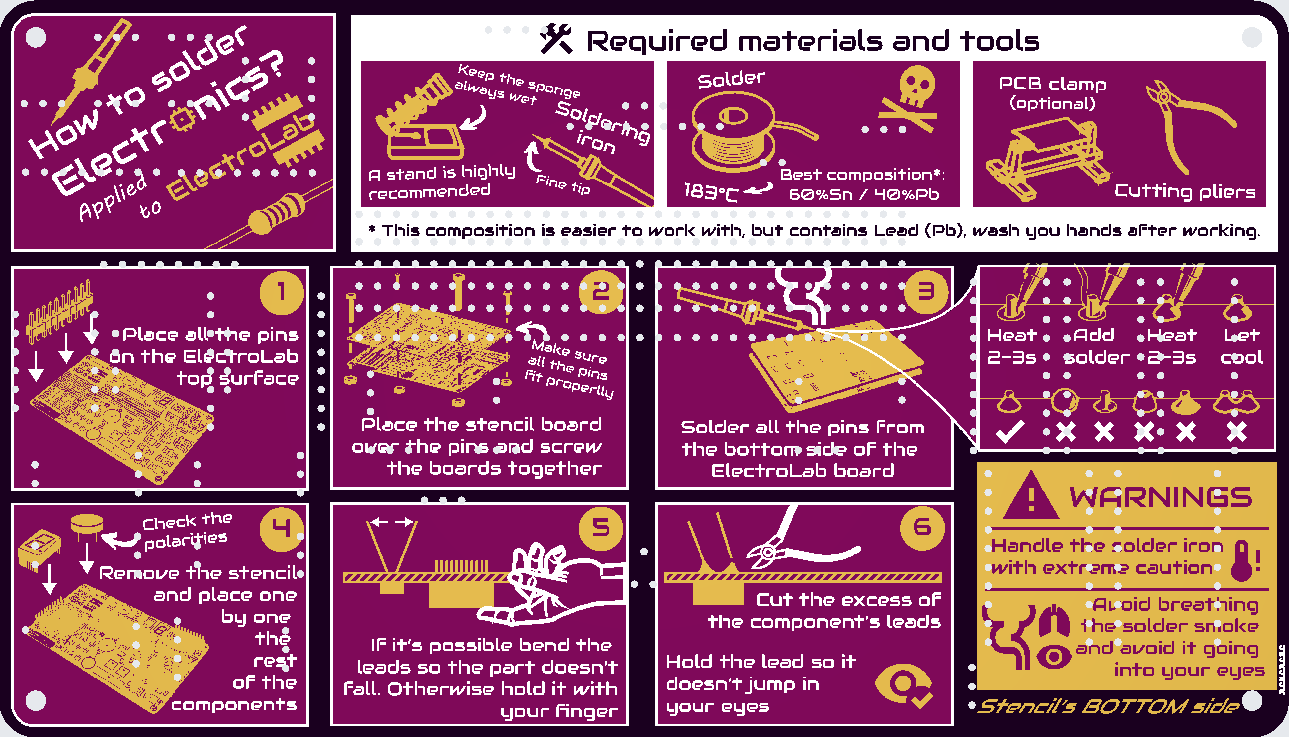
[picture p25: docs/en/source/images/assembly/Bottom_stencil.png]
    

Steps
-----

1. Mount 2 screws on the |Product| diagonally, with the screw head comming from the bottom side (the one with :term:`SMD` components) and add a nut on the top side of the board (the one with the QR code).

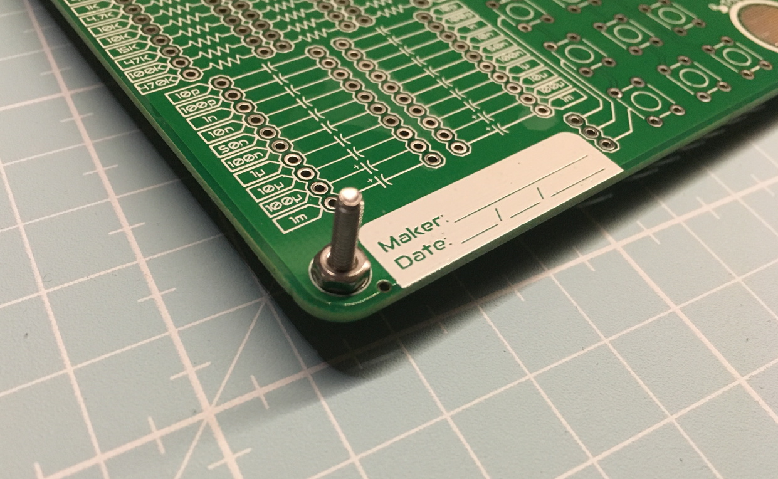
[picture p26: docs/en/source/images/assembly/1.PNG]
    

2. Start with the pinheads. Place **all** the pinheads on the |Product| top side. Make sure you introduce the short side of the pin on the :term:`PCB`.

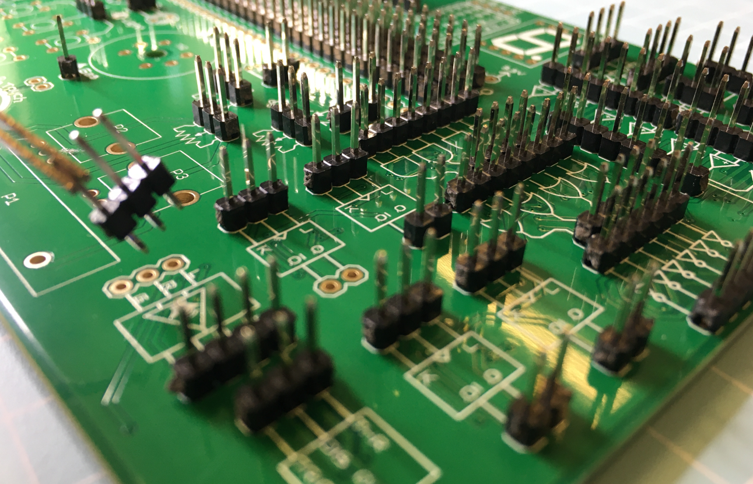
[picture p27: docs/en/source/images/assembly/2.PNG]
    

3. Once you have mounted all the pins, place gently the *Stencil board* over it. Be patient, some pins (like the individual pin from the signal generator or the Gas sensor) may become troubly rebels. Once they are all in place, screw the other 2 nuts to the screws to secure the two boards together.

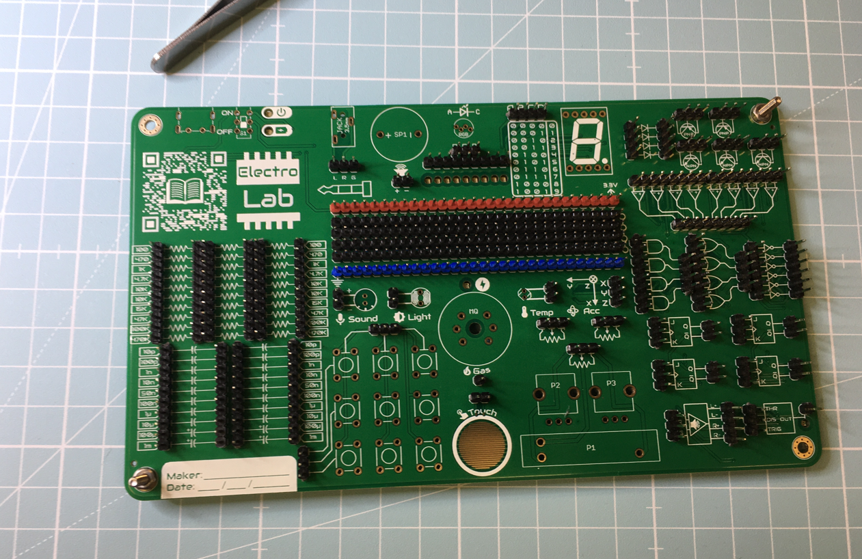
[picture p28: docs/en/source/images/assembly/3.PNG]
    

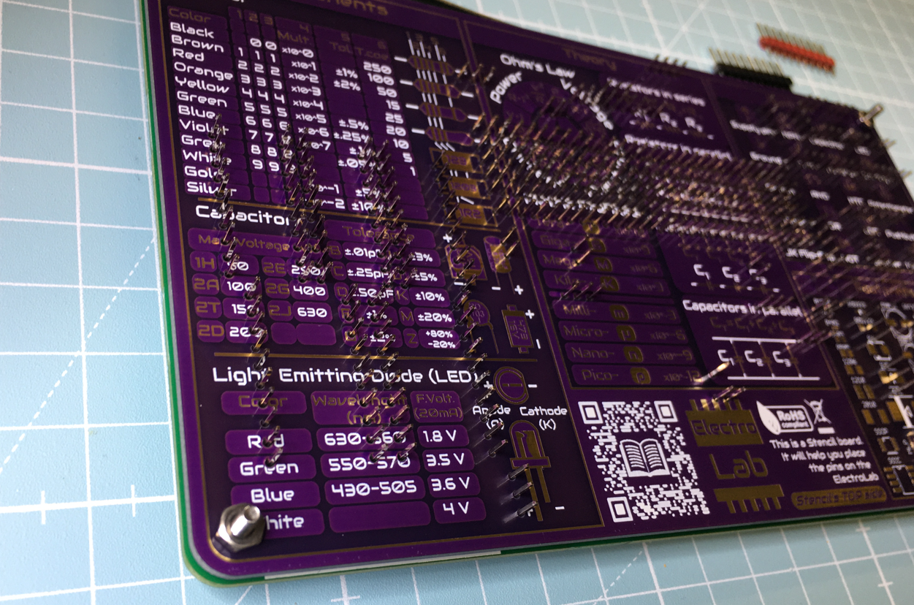
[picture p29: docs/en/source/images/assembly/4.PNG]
    

4. With the pinheads correctly secured, proceed to the soldering of each individual pin on the **ElectroLab's bottom side**. Pay special attention to those solderings close to :term:`SMD` components for avoiding any damage.
    
    
        
5. After soldering all the pinheads, the screws can be removed and the boards separated.

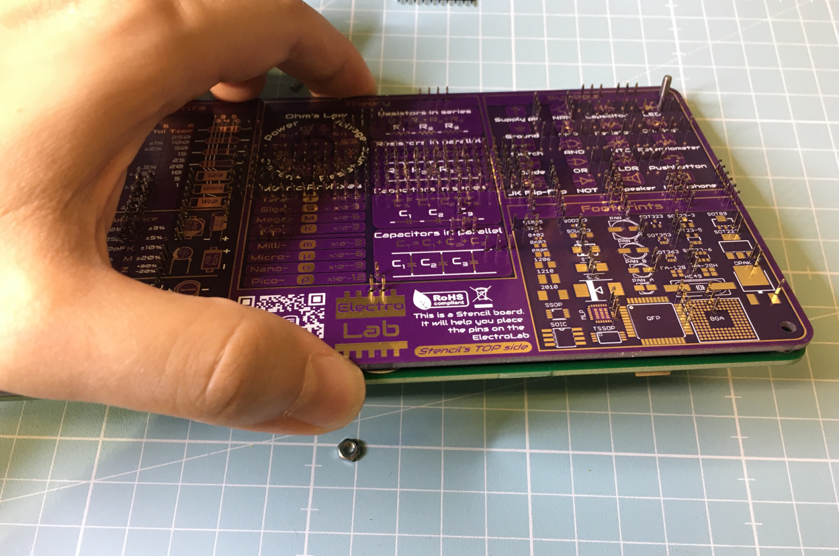
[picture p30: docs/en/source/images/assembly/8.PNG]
    
        
6. Continue with each individual :term:`THT` component, starting from the smaller like the switches and sensors. In this case is highly recomended to:

    .. WARNING:: 
        Some components have **polarity**, which means they have to be assembled on a specific way, pay attention to the marks under the sensor.
        Those :term:`THT` components are the speaker, the microphone, the RGB led and the 7 segments display.

    1. Place the component on top side of the board

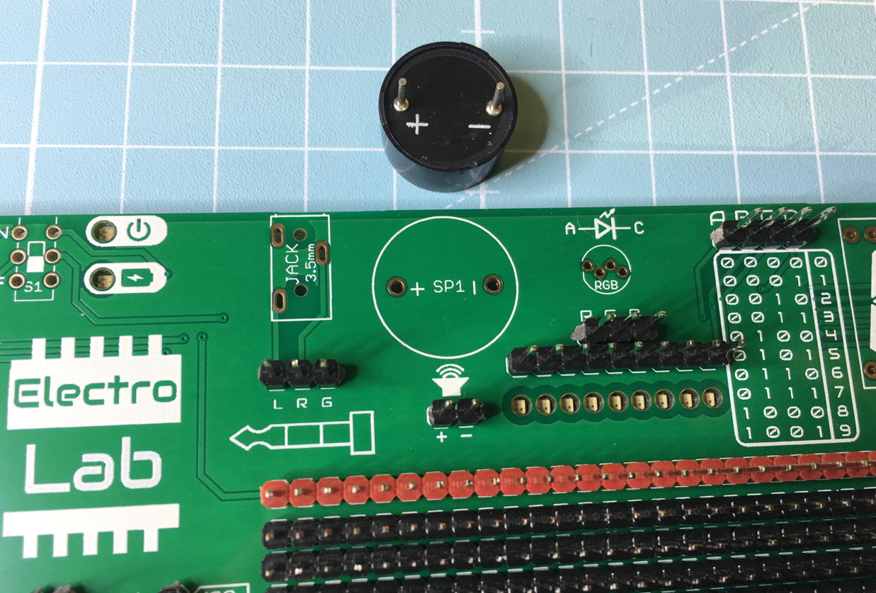
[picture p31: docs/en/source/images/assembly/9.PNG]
        

    2. If it has long pins that can bend (like the :term:`LDR` sensor), bend the pins to keep it in place. 
    If not, press it to hold it in position while soldering (like the speaker).

    3. Start by soldering just one of the pins. 
            
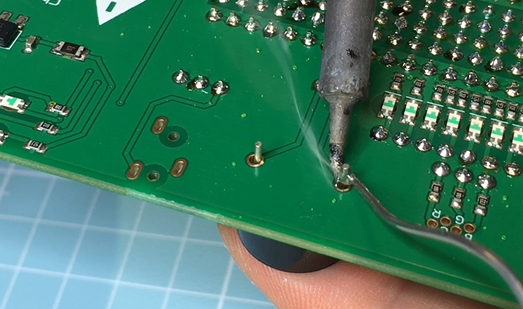
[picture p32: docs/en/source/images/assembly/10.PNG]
        

    4. Check if the sensor is still in the correct position and correct it if not.
    5. Solder the rest of the pins and cut the excess length of them.
            
        

    .. Attention:: 
        Please exercise caution when trimming the excess metal from soldered pins.  
        Wearing safety glasses or goggles while performing this task is strongly recommended to avoid potential eye injury.

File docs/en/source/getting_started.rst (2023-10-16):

💡 Getting started
===============

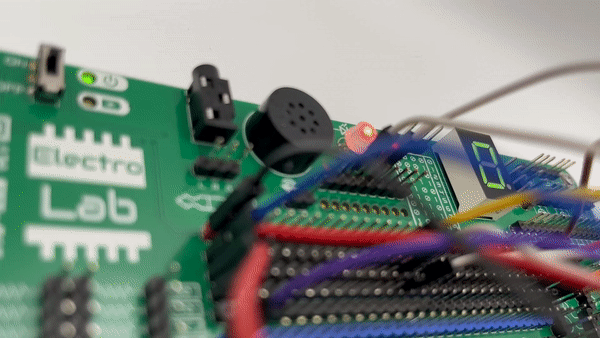
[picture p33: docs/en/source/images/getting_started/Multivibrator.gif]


    Oscillating circuit

The ElectroLab board is being sold as a kit, which means that you will need to assemble (and solder) it. The first thing to do once you 
receive your kit, is making sure you find all the components included:

1. ElectroLab board (green PCB)
2. Stencil board (purple PCB)
3. Female-to-female jumper boards (pack of 40)
4. THT components:

    - 2x Rotary potentiometers
    - 1x Linear potentiometer
    - 1x Speaker
    - 1x 7 segments display
    - 1x RGB led
    - 1x Slide switch
    - 1x USB-C connector
    - 1x NTC thermistor
    - 1x LDR photoresistor
    - 1x Microphone
    - 9x Pushbutton
    - 1x 3.5mm jack connector
    - 1x MQ-2 gas sensor
    - 1x Blue header
    - 1x Red header
    - 10x Black header

and optionally you could have acquired:

- A 1000mAh LiPo battery
- A protection enclosure consisting on:

    - 3 transparent acrylic plates
    - 4 screws set (screw, washer & nut)

After assembling it (visit the :doc:`assembly` section), you will be able to make your own circuits 
or start exploring the ones on the :doc:`examples` section.

🎓How it works?
-------------
On the |Product|, each component is internally powered and it's :term:`I/O` are already routed to an accessible pinhead. 
This makes it very easy the quick prototyping of electronic circuits since you just need to interconnect them with female-female wires.

While working with the |Product|, make sure you follow this steps:

- ✅ Analyze and understand the schematic you want to assembly with the |Product|

- ✅ Check if you will be using polarized components (like the polarized capacitors or the microphone) for paying extra attention.

- ✅ Before plugging or unplugging any jumper wires, make sure the board is turned off:

- ✅ Assembly the circuit following a known order, it will save you time in case you get lost.

- ✅ Check that there are not any wire connecting 3.3V to :term:`GND`.

- ✅ Connect the USB cable or the Auxiliar Interface in order to power the board.

- ✅ Toggle the switch and check that the power led turns on.

- ✅ Play with your recently assembled circuit and experiment with safety!

.. Caution::
    If the Power LED indicator doesn't turn on, power off the board and check the circuit: you might have 
    a shortcircuit somewhere!

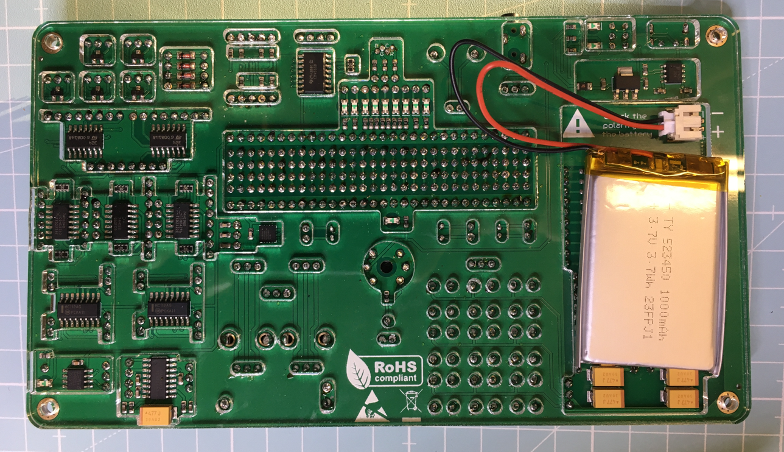
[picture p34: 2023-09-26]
docs/es/source/images/assembly/15.PNG

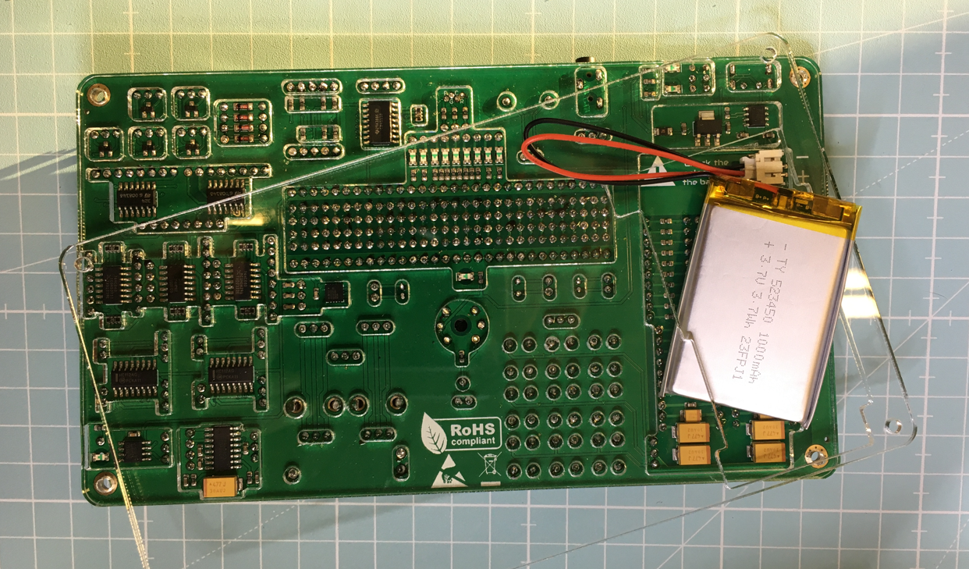
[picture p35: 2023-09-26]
docs/es/source/images/assembly/16.PNG

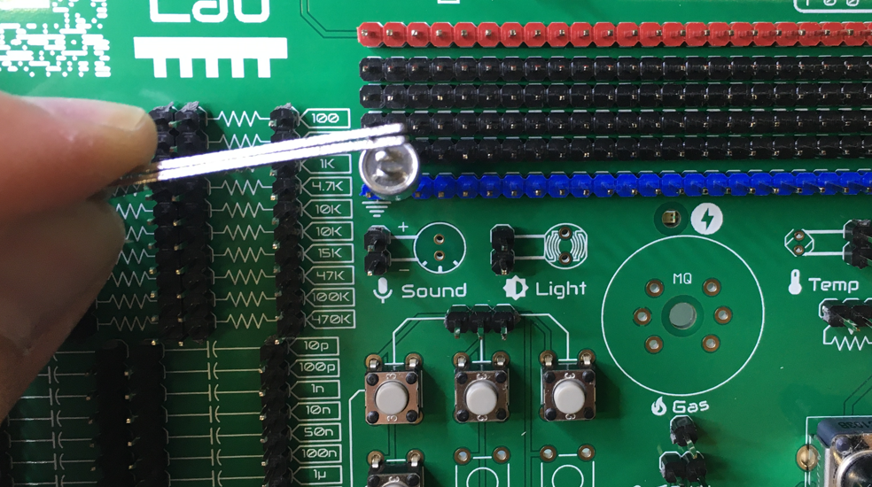
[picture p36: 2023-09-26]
docs/en/source/images/assembly/12.PNG

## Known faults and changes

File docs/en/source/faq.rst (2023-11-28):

💬 :term:`FAQ`
=============================

After connecting everything and turning on the |Product|, I don't see any :term:`LED` on.
    If the board is correctly powered and you cannot see the power :term:`LED` on, disconnect the power immediately: 
    there is a short-circuit in your board, meaning that there is a wire (with very little resistance) connecting the 
    Vcc (3.3V) and the :term:`GND`.

After assembling everything and powering the board, the circuit doesn’t do what I expected, why?
    The more complex the assembled circuit is, the easier to make a mistake. If the circuit has 
    been tested before, the most likely answer is that there is some error at a certain connection. 
    The solution is to check node by node that everything is correctly connected.

I accidentally inverted the polarity of a component that was marked as polarized, what can I do?
    If the component seems damaged from outside or the circuit doesn’t work after fixing it, it 
    is clear that you will need to replace it or send it for repair (check :ref:`support`).

I want to expand the set of sensors to play with other, can I do it?
    Of course! Just make sure are components rated for 3.3V. Remember to connect both :term:`GND` 
    together and in case the sensor needs a power supply connect it to the 3.3V bus-bar.

Can I connect multiple ElectroLab together for making more complex circuits?
    Yes, some of the circuits can become so complex that you might need to do it like this. In 
    this case just connect the 3.3V of one ElectroLab to the 3.3V of the other and the :term:`GND` of one to 
    the :term:`GND` of the other, so both are powered correctly.

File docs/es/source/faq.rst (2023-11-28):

💬 :term:`FAQ`
=============================

Después de conectar todo y encender el |Product|, no veo ningún :term:`LED`.
    Si la placa está correctamente alimentada y no puedes ver el :term:`LED` de encendido, desconecta la alimentación inmediatamente:
    hay un cortocircuito en tu placa, lo que significa que hay un cable (con muy poca resistencia) conectando el
    Vcc y :term:`GND`.

Después de ensamblar todo y encender la placa, el circuito no hace lo que esperaba, ¿por qué?
    Cuanto más complejo sea el circuito ensamblado, más fácil será cometer un error. Si el circuito ha sido probado antes, lo más probable es que haya algún error en alguna conexión.
    La solución es verificar nodo por nodo que todo esté correctamente conectado.

Invertí accidentalmente la polaridad de un componente que estaba marcado como polarizado, ¿qué puedo hacer?
    Si el componente parece dañado por fuera o el circuito no funciona después de arreglarlo, está claro que necesitarás reemplazarlo o enviarlo para reparación (consulta :ref:`support`).

Quiero ampliar el conjunto de sensores para probar otros, ¿puedo hacerlo?
    ¡Por supuesto! Solo asegúrate de que los componentes estén calificados para 3.3V. Recuerda conectar ambos :term:`GND`
    juntos y, en caso de que el sensor necesite una fuente de alimentación, conéctalo a la barra colectora de 3.3V.

¿Puedo conectar varios ElectroLab para hacer circuitos más complejos?
    Sí, algunos circuitos pueden volverse tan complejos que es posible que necesites hacerlo de esta manera. En
    este caso, simplemente conecta el 3.3V de un ElectroLab al 3.3V del otro y el :term:`GND` de uno al
    :term:`GND` del otro, para que ambos estén alimentados correctamente.

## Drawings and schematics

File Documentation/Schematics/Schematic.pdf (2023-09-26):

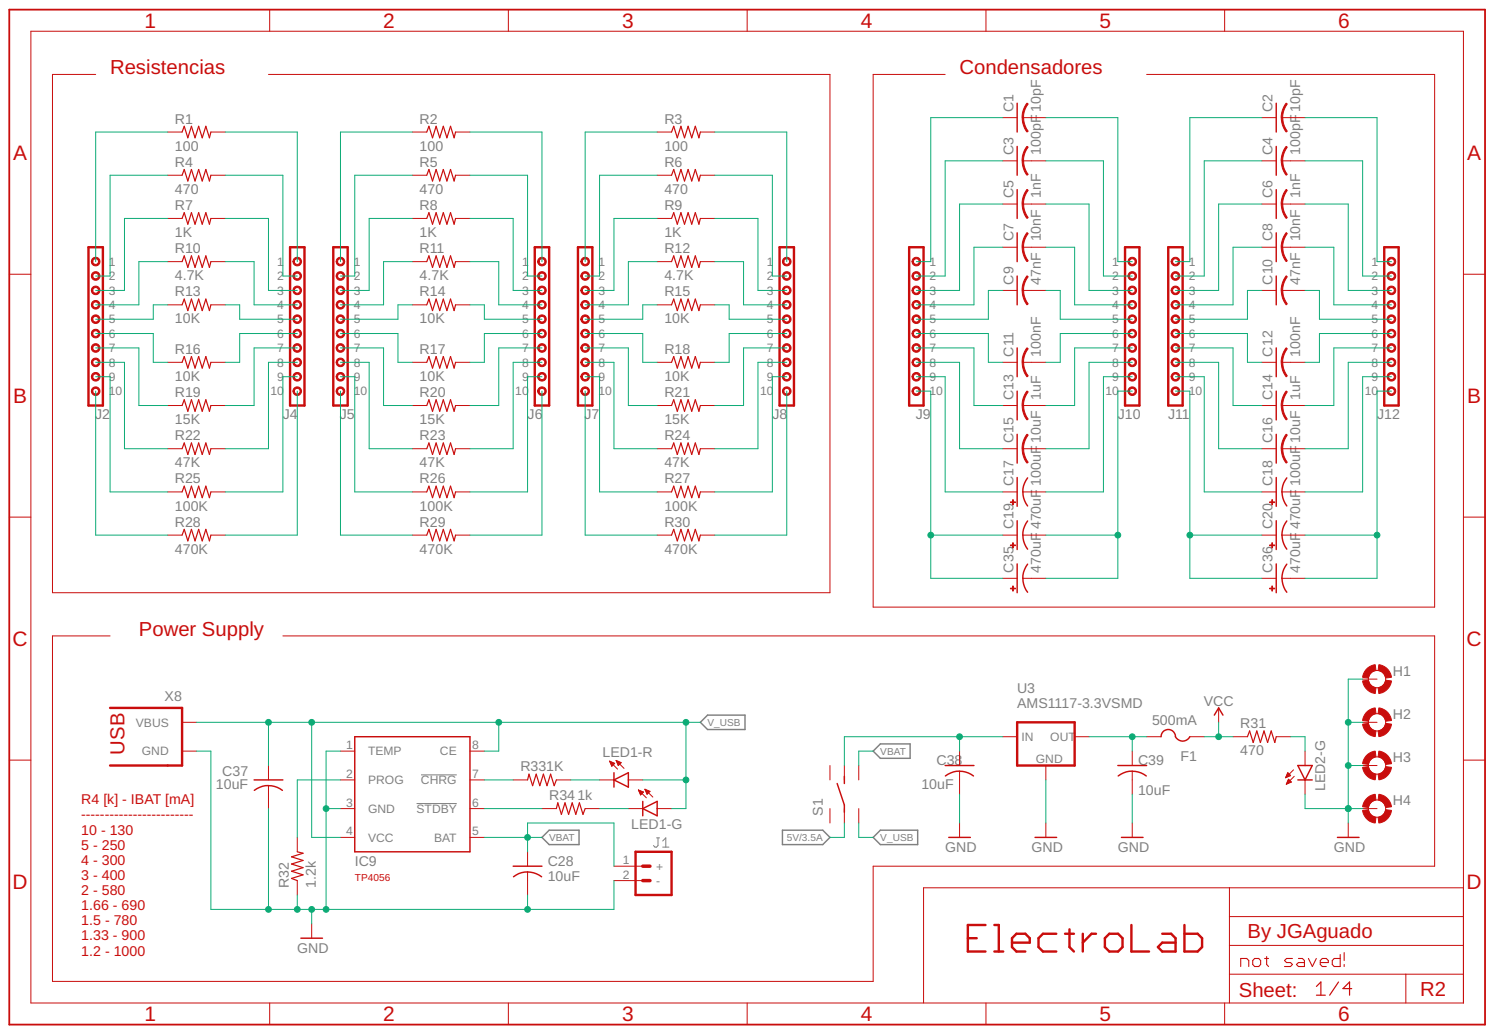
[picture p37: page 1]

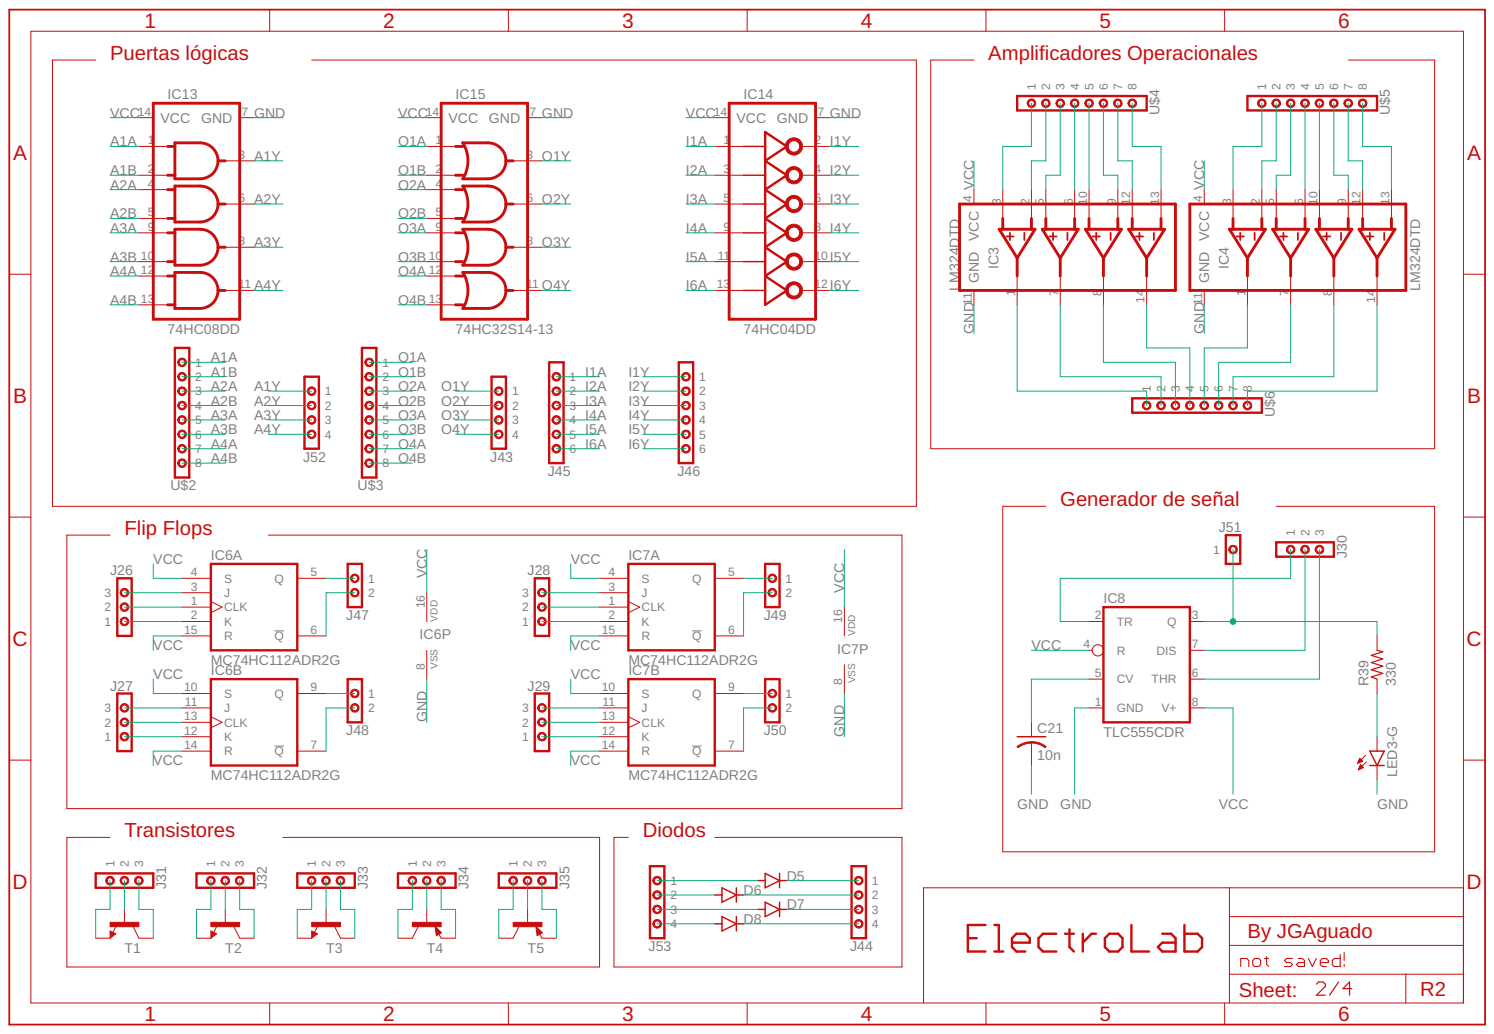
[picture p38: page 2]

Puertas lógicas | | Amplificadores Operacionales

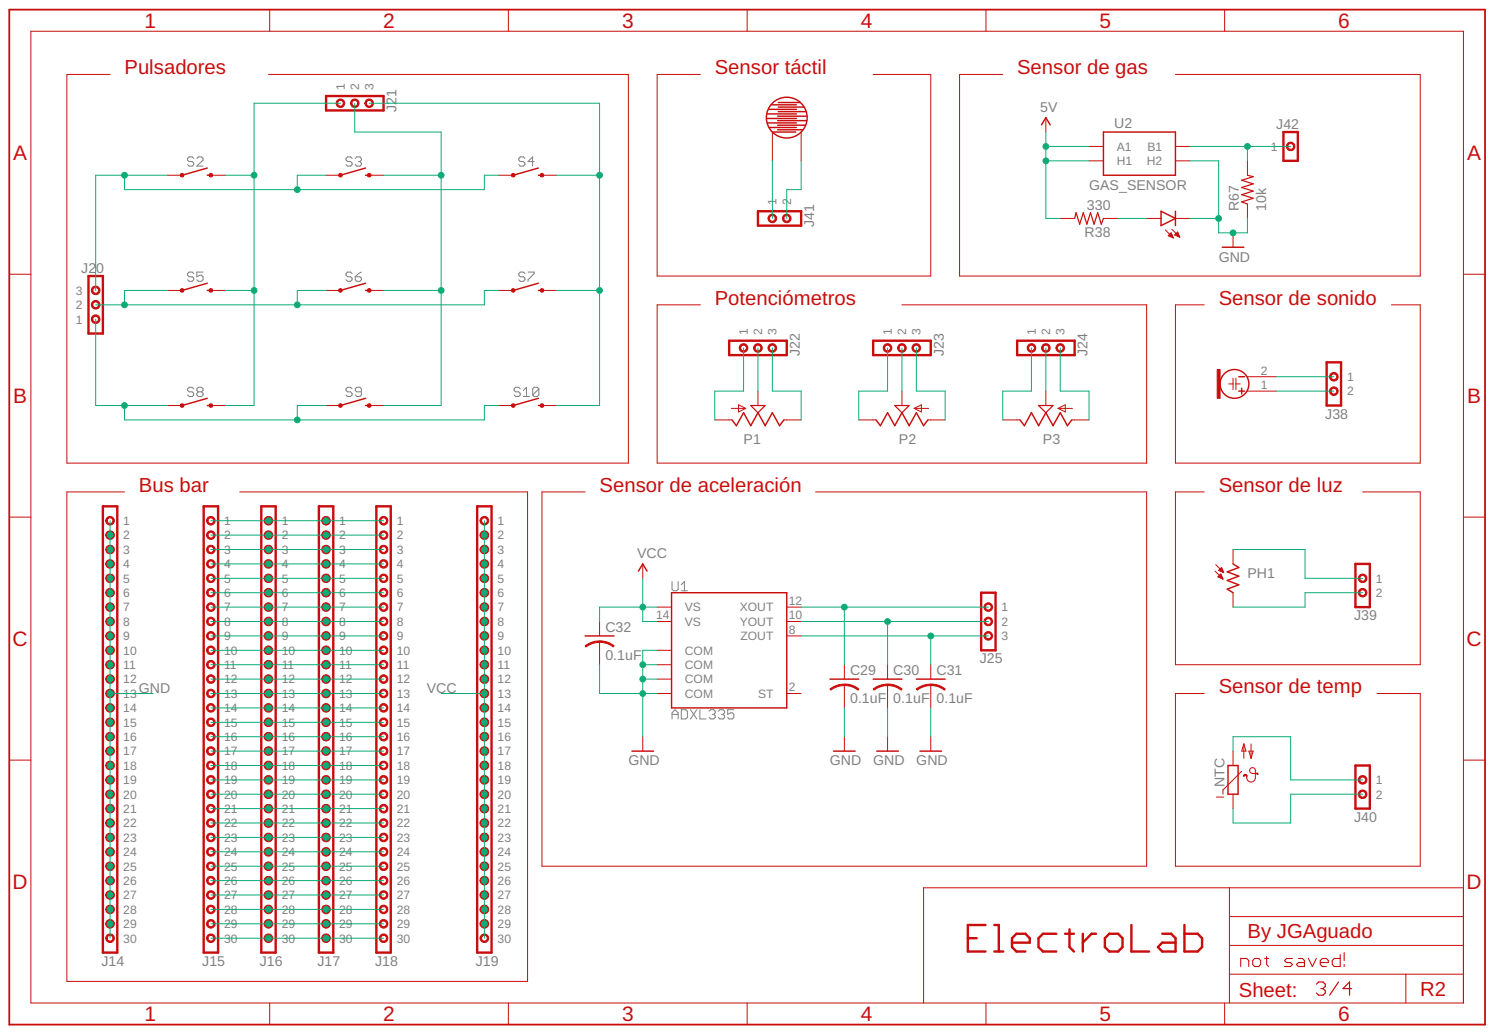
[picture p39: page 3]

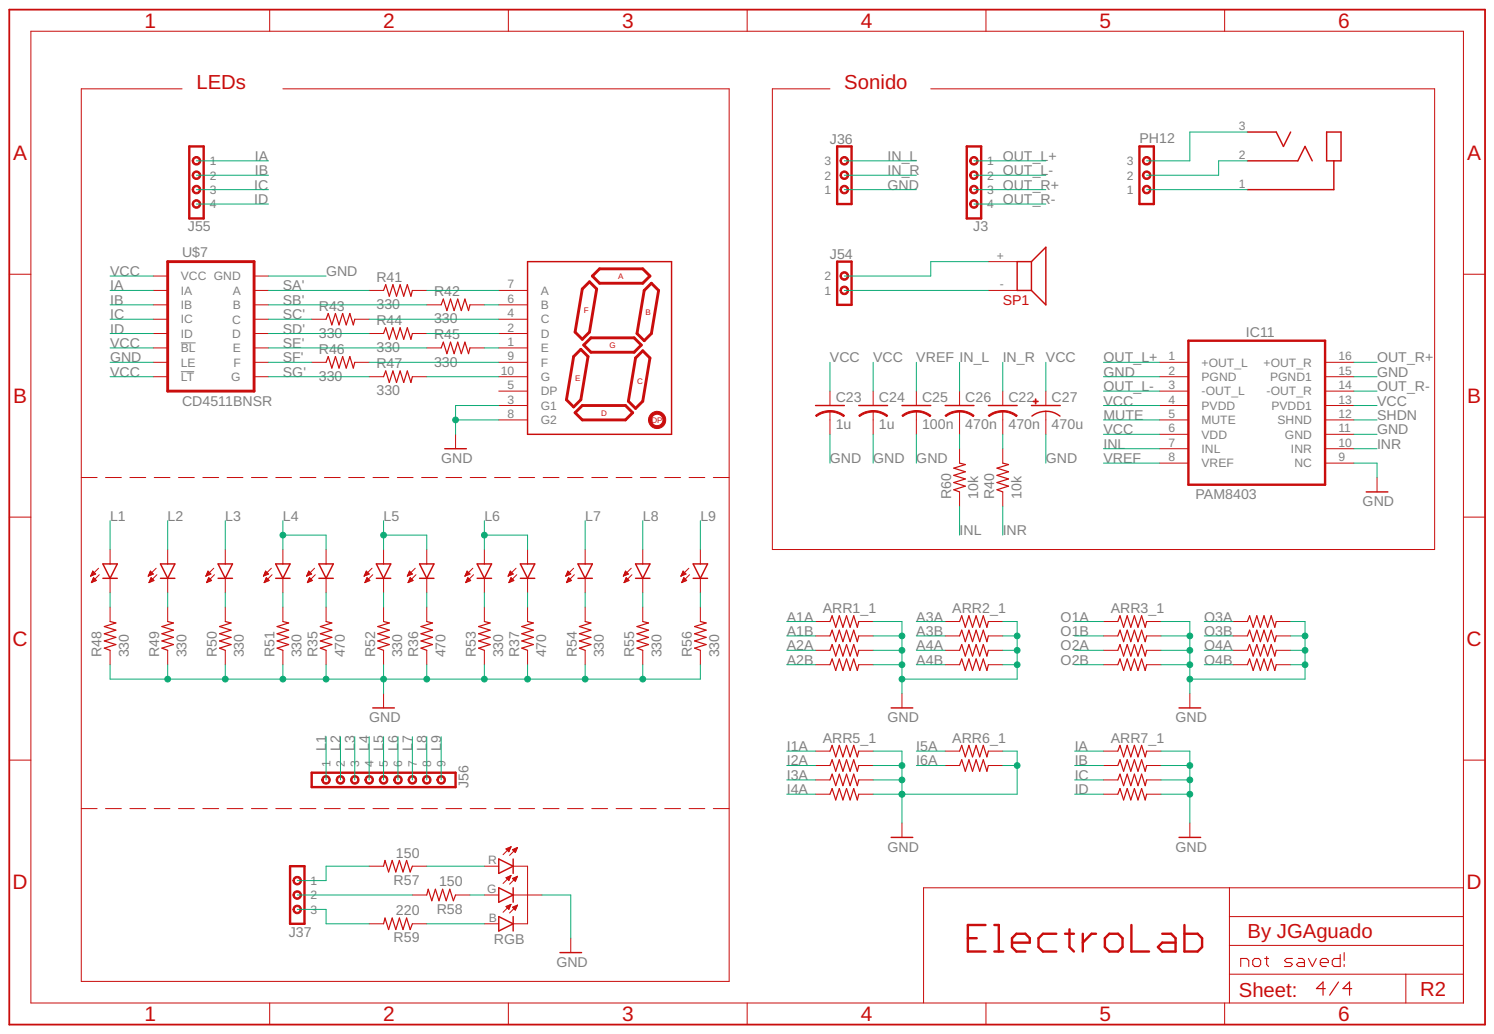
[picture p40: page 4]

C GND

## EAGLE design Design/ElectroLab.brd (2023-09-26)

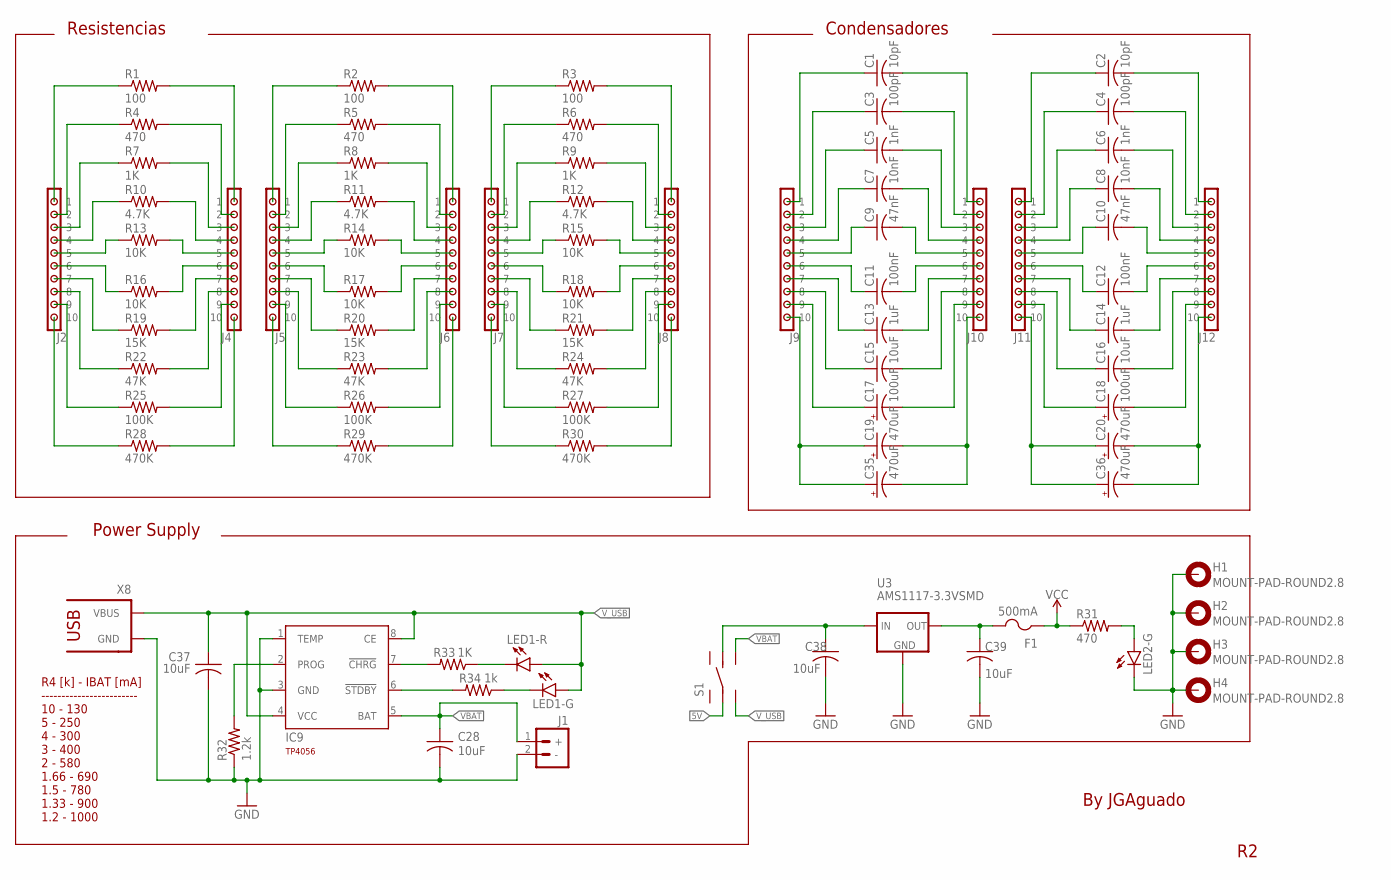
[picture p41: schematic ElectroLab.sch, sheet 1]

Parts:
C1, C2: 10pF; 0603
C3, C4: 100pF; 0603
C5, C6: 1nF; 0603
C7, C8: 10nF; 0603
C9, C10: 47nF; 0603
C11, C12: 100nF; 0603
C13, C14: 1uF; 0603
C15, C16: 10uF; 0603
C17, C18: 100uF; B/3528-21R; LCSC C16133
C19, C20, C35, C36: 470uF; D/7343-31R
C28, C37, C38, C39: 10uF; C0603
F1: 500mA; R1206; LCSC C355568
H1, H2, H3, H4: MOUNT-PAD-ROUND2.8; 2,8-PAD
IC9: TP4056; SOT23-8; LCSC C16581
J1: BAT_CONN-JST-2MM-SMT; JST-2-SMD; LCSC C3029440
J2, J4, J5, J6, J7, J8, J9, J10, J11, J12: CONN_10"; 1X10
LED1, LED2: E6CC1205RYGC2UDA; BICOLOR_LED
R1, R2, R3: 100; 0603
R4, R5, R6, R31: 470; 0603
R7, R8, R9, R33: 1K; 0603
R10, R11, R12: 4.7K; 0603
R13, R14, R15, R16, R17, R18: 10K; 0603
R19, R20, R21: 15K; 0603
R22, R23, R24: 47K; 0603
R25, R26, R27: 100K; 0603
R28, R29, R30: 470K; 0603
R32: 1.2k; R0603
R34: 1k; 0603
S1: DPDT_JS202011CQN
U3: AMS1117-3.3VSMD; SOT223
X8: USB-C-POWER

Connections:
5V: S1.2 (LC); also elsewhere on the board
GND: C28.2, C37.2, C38.2, C39.2, H1.B2,8, H2.B2,8, H3.B2,8, H4.B2,8, IC9.1 (TEMP), IC9.3 (GND), J1.2 (-), LED2.1 (C), R32.1, U3.1 (GND), X8.GND; also elsewhere on the board
unnamed: J2.1, R1.1
unnamed: J2.2, R4.1
unnamed: J2.3, R7.1
unnamed: J2.4, R10.1
unnamed: J2.5, R13.1
unnamed: J2.6, R16.1
unnamed: J2.7, R19.1
unnamed: J2.8, R22.1
unnamed: J2.9, R25.1
unnamed: J2.10, R28.1
unnamed: J4.10, R28.2
unnamed: J4.9, R25.2
unnamed: J4.8, R22.2
unnamed: J4.7, R19.2
unnamed: J4.5, R13.2
unnamed: J4.6, R16.2
unnamed: J4.4, R10.2
unnamed: J4.3, R7.2
unnamed: J4.2, R4.2
unnamed: J4.1, R1.2
unnamed: J5.1, R2.1
unnamed: J5.2, R5.1
unnamed: J5.3, R8.1
unnamed: J5.4, R11.1
unnamed: J5.5, R14.1
unnamed: J5.6, R17.1
unnamed: J5.7, R20.1
unnamed: J5.8, R23.1
unnamed: J5.9, R26.1
unnamed: J5.10, R29.1
unnamed: J6.10, R29.2
unnamed: J6.9, R26.2
unnamed: J6.8, R23.2
unnamed: J6.7, R20.2
unnamed: J6.6, R17.2
unnamed: J6.5, R14.2
unnamed: J6.4, R11.2
unnamed: J6.3, R8.2
unnamed: J6.2, R5.2
unnamed: J6.1, R2.2
unnamed: J7.1, R3.1
unnamed: J7.2, R6.1
unnamed: J7.3, R9.1
unnamed: J7.4, R12.1
unnamed: J7.5, R15.1
unnamed: J7.6, R18.1
unnamed: J7.7, R21.1
unnamed: J7.8, R24.1
unnamed: J7.9, R27.1
unnamed: J7.10, R30.1
unnamed: J8.10, R30.2
unnamed: J8.9, R27.2
unnamed: J8.8, R24.2
unnamed: J8.7, R21.2
unnamed: J8.6, R18.2
unnamed: J8.5, R15.2
unnamed: J8.4, R12.2
unnamed: J8.3, R9.2
unnamed: J8.2, R6.2
unnamed: J8.1, R3.2
unnamed: C1.1, J9.1
unnamed: C3.1, J9.2
unnamed: C5.1, J9.3
unnamed: C7.1, J9.4
unnamed: C9.1, J9.5
unnamed: C11.1, J9.6
unnamed: C13.1, J9.7
unnamed: C15.1, J9.8
unnamed: C17.+, J9.9
unnamed: C19.+, C35.+, J9.10
unnamed: C1.2, J10.1
unnamed: C3.2, J10.2
unnamed: C5.2, J10.3
unnamed: C7.2, J10.4
unnamed: C9.2, J10.5
unnamed: C11.2, J10.6
unnamed: C13.2, J10.7
unnamed: C15.2, J10.8
unnamed: C17.-, J10.9
unnamed: C19.-, C35.-, J10.10
unnamed: C2.1, J11.1
unnamed: C4.1, J11.2
unnamed: C6.1, J11.3
unnamed: C8.1, J11.4
unnamed: C10.1, J11.5
unnamed: C12.1, J11.6
unnamed: C14.1, J11.7
unnamed: C16.1, J11.8
unnamed: C18.+, J11.9
unnamed: C20.+, C36.+, J11.10
unnamed: C20.-, C36.-, J12.10
unnamed: C18.-, J12.9
unnamed: C16.2, J12.8
unnamed: C14.2, J12.7
unnamed: C12.2, J12.6
unnamed: C10.2, J12.5
unnamed: C8.2, J12.4
unnamed: C6.2, J12.3
unnamed: C4.2, J12.2
unnamed: C2.2, J12.1
unnamed: LED2.2 (A), R31.2
unnamed: IC9.6 (!STDBY), R34.2
unnamed: LED1.4 (C), R33.1
unnamed: LED1.1 (C), R34.1
unnamed: IC9.2 (PROG), R32.2
unnamed: IC9.7 (!CHRG), R33.2
unnamed: C38.1, S1.5 (RC), U3.3 (IN)
VBAT: C28.1, IC9.5 (BAT), J1.1 (+), S1.6 (R2)
VCC: F1.1, R31.1; also elsewhere on the board
VOUT: C39.1, F1.2, U3.2 (OUT)
V_USB: C37.1, IC9.4 (VCC), IC9.8 (CE), LED1.2 (A), LED1.3 (A), S1.3 (L2), X8.VBUS

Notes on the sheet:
By JGAguado
Condensadores
Resistencias
Power Supply
R4 [k] - IBAT [mA] ------------------------ 10 - 130 5 - 250 4 - 300 3 - 400 2 - 580 1.66 - 690 1.5 - 780 1.33 - 900 1.2 - 1000

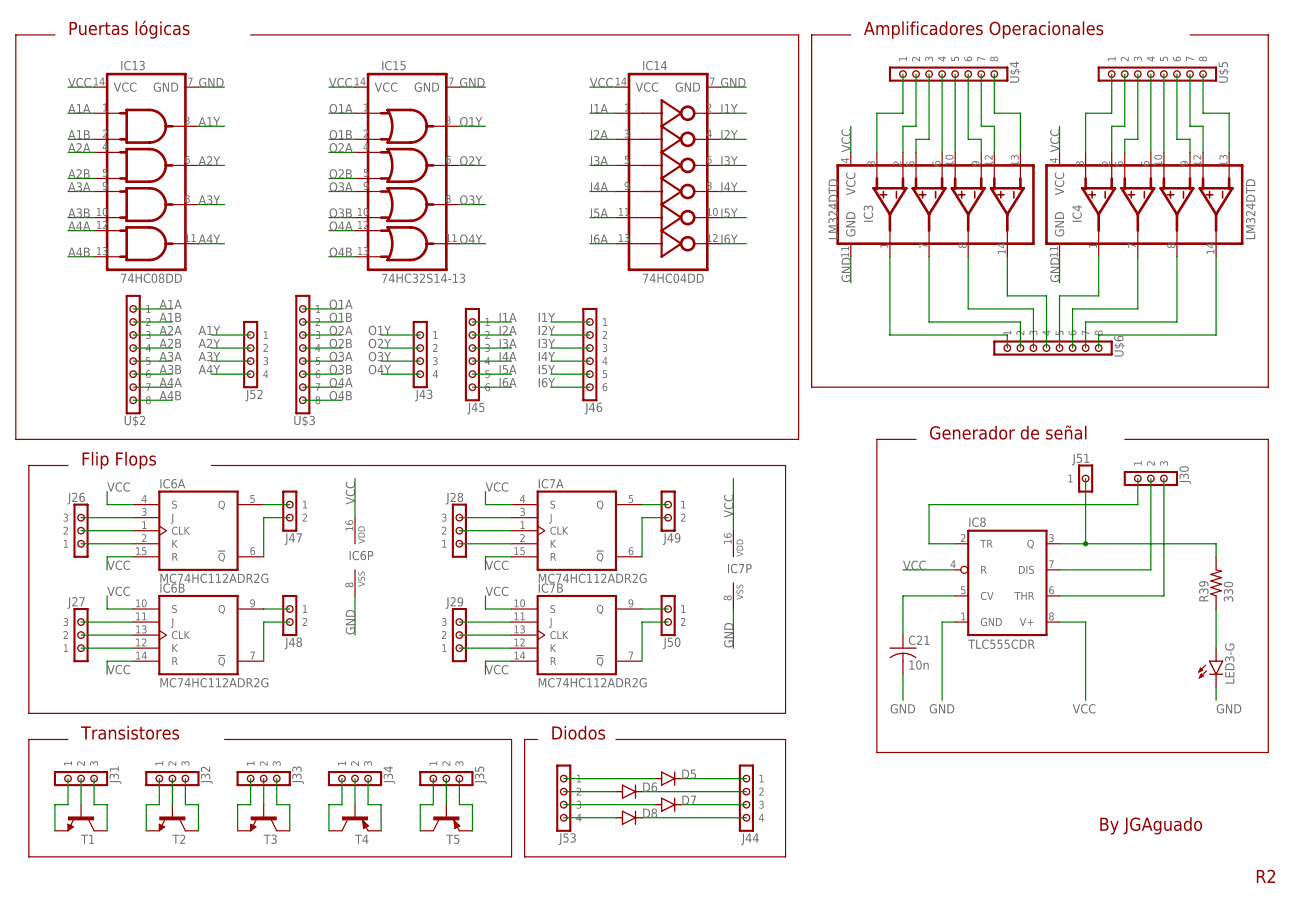
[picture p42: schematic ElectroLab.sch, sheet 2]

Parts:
C21: 10n; 0603
D5, D6, D7, D8: LL4148; LL-34
IC3, IC4: LM324DTD; SO14
IC6, IC7: MC74HC112ADR2G; SO16
IC8: TLC555CDR; SO08; LCSC C6986
IC13: 74HC08DD; SO14
IC14: 74HC04DD; SO14
IC15: 74HC32S14-13; SO14; LCSC C176921
J26, J27, J28, J29, J30, J31, J32, J33, J34, J35: CONN_03; 1X03
J43, J44, J52, J53: CONN_04; 1X04
J45, J46: CONN_06; 1X06
J47, J48, J49, J50: CONN_02; 1X02
J51: CONN_01; 1X01
LED3: E6CC1205RYGC2UDA; BICOLOR_LED
R39: 330; 0603
T1: MMBT2222A; SOT23
T2, T3: T_NPNMMBT2222A-1P_CHANGJ_SOT23-BEC; SOT23
T4, T5: T_PNPMMBT5401_CHANGJ_SOT23-BEC; SOT23
U$2, U$3, U$4, U$5, U$6: CONN_08; 1X08

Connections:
A1A: IC13.1 (1A), U$2.1; also elsewhere on the board
A1B: IC13.2 (1B), U$2.2; also elsewhere on the board
A1Y: IC13.3 (1Y), J52.1
A2A: IC13.4 (2A), U$2.3; also elsewhere on the board
A2B: IC13.5 (2B), U$2.4; also elsewhere on the board
A2Y: IC13.6 (2Y), J52.2
A3A: IC13.9 (3A), U$2.5; also elsewhere on the board
A3B: IC13.10 (3B), U$2.6; also elsewhere on the board
A3Y: IC13.8 (3Y), J52.3
A4A: IC13.12 (4A), U$2.7; also elsewhere on the board
A4B: IC13.13 (4B), U$2.8; also elsewhere on the board
A4Y: IC13.11 (4Y), J52.4
GND: C21.2, IC3.11 (GND), IC4.11 (GND), IC6.8 (VSS), IC7.8 (VSS), IC8.1 (GND), IC13.7 (GND), IC14.7 (GND), IC15.7 (GND), LED3.1 (C); also elsewhere on the board
I1A: IC14.1 (1A), J45.1; also elsewhere on the board
I1Y: IC14.2 (1Y), J46.1
I2A: IC14.3 (2A), J45.2; also elsewhere on the board
I2Y: IC14.4 (2Y), J46.2
I3A: IC14.5 (3A), J45.3; also elsewhere on the board
I3Y: IC14.6 (3Y), J46.3
I4A: IC14.9 (4A), J45.4; also elsewhere on the board
I4Y: IC14.8 (4Y), J46.4
I5A: IC14.11 (5A), J45.5; also elsewhere on the board
I5Y: IC14.10 (5Y), J46.5
I6A: IC14.13 (6A), J45.6; also elsewhere on the board
I6Y: IC14.12 (6Y), J46.6
unnamed: D8.A, J53.4
unnamed: D8.C, J44.4
unnamed: D5.A, J53.1
unnamed: IC6.5 (Q), J47.1
unnamed: IC6.9 (Q), J48.1
unnamed: IC7.5 (Q), J49.1
unnamed: IC7.9 (Q), J50.1
unnamed: LED3.2 (A), R39.1
unnamed: IC3.3 (1+), U$4.1
unnamed: IC3.2 (1-), U$4.2
unnamed: IC3.5 (2+), U$4.3
unnamed: IC3.6 (2-), U$4.4
unnamed: IC3.10 (3+), U$4.5
unnamed: IC3.9 (3-), U$4.6
unnamed: IC3.12 (4+), U$4.7
unnamed: IC3.13 (4-), U$4.8
unnamed: IC4.3 (1+), U$5.1
unnamed: IC6.2 (K), J26.1
unnamed: IC6.1 (CLK), J26.2
unnamed: IC6.3 (J), J26.3
unnamed: IC6.12 (K), J27.1
unnamed: IC6.13 (CLK), J27.2
unnamed: IC6.11 (J), J27.3
unnamed: IC7.2 (K), J28.1
unnamed: IC7.1 (CLK), J28.2
unnamed: IC7.3 (J), J28.3
unnamed: IC7.12 (K), J29.1
unnamed: IC7.13 (CLK), J29.2
unnamed: IC7.11 (J), J29.3
unnamed: IC6.6 (!Q), J47.2
unnamed: IC6.7 (!Q), J48.2
unnamed: IC7.6 (!Q), J49.2
unnamed: IC7.7 (!Q), J50.2
unnamed: D7.A, J53.3
unnamed: D6.A, J53.2
unnamed: IC4.2 (1-), U$5.2
unnamed: IC4.5 (2+), U$5.3
unnamed: IC4.6 (2-), U$5.4
unnamed: IC4.10 (3+), U$5.5
unnamed: IC4.9 (3-), U$5.6
unnamed: IC4.12 (4+), U$5.7
unnamed: IC4.13 (4-), U$5.8
unnamed: IC3.1 (1Y), U$6.1
unnamed: IC3.7 (2Y), U$6.2
unnamed: IC3.8 (3Y), U$6.3
unnamed: IC3.14 (4Y), U$6.4
unnamed: IC4.1 (1Y), U$6.5
unnamed: IC4.7 (2Y), U$6.6
unnamed: D5.C, J44.1
unnamed: IC4.8 (3Y), U$6.7
unnamed: IC4.14 (4Y), U$6.8
unnamed: D6.C, J44.2
unnamed: D7.C, J44.3
unnamed: J31.1, T1.2 (E)
unnamed: J31.2, T1.1 (B)
unnamed: J31.3, T1.3 (C)
unnamed: J32.1, T2.2 (E)
unnamed: J32.2, T2.1 (B)
unnamed: J32.3, T2.3 (C)
unnamed: J33.1, T3.2 (E)
unnamed: J33.2, T3.1 (B)
unnamed: J33.3, T3.3 (C)
unnamed: J34.1, T4.3 (C)
unnamed: J34.2, T4.1 (B)
unnamed: J34.3, T4.2 (E)
unnamed: J35.1, T5.3 (C)
unnamed: J35.2, T5.1 (B)
unnamed: J35.3, T5.2 (E)
unnamed: IC8.2 (TR), J30.1
unnamed: IC8.3 (Q), J51.1, R39.2
unnamed: C21.1, IC8.5 (CV)
unnamed: IC8.7 (DIS), J30.2
unnamed: IC8.6 (THR), J30.3
O1A: IC15.1 (1A), U$3.1; also elsewhere on the board
O1B: IC15.2 (1B), U$3.2; also elsewhere on the board
O1Y: IC15.3 (1Y), J43.1
O2A: IC15.4 (2A), U$3.3; also elsewhere on the board
O2B: IC15.5 (2B), U$3.4; also elsewhere on the board
O2Y: IC15.6 (2Y), J43.2
O3A: IC15.9 (3A), U$3.5; also elsewhere on the board
O3B: IC15.10 (3B), U$3.6; also elsewhere on the board
O3Y: IC15.8 (3Y), J43.3
O4A: IC15.12 (4A), U$3.7; also elsewhere on the board
O4B: IC15.13 (4B), U$3.8; also elsewhere on the board
O4Y: IC15.11 (4Y), J43.4
VCC: IC3.4 (VCC), IC4.4 (VCC), IC6.4 (S), IC6.10 (S), IC6.14 (R), IC6.15 (R), IC6.16 (VDD), IC7.4 (S), IC7.10 (S), IC7.14 (R), IC7.15 (R), IC7.16 (VDD), IC8.4 (R), IC8.8 (V+), IC13.14 (VCC), IC14.14 (VCC), IC15.14 (VCC); also elsewhere on the board

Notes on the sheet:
Puertas lógicas
Amplificadores Operacionales
Flip Flops
Transistores
Diodos
Generador de señal
By JGAguado

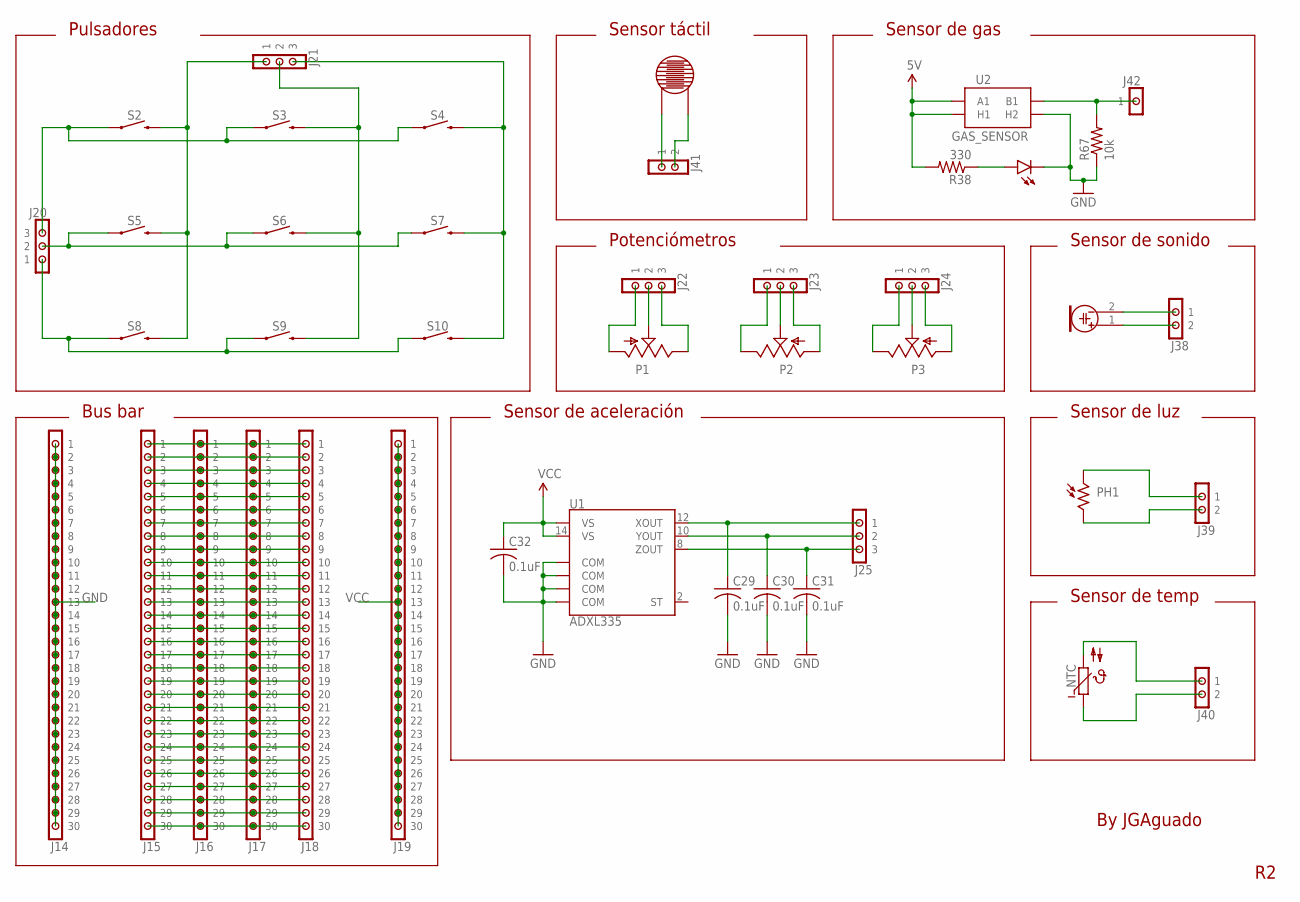
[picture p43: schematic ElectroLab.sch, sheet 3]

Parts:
C29, C30, C31, C32: 0.1uF; 0603
J14, J15, J16, J17, J18, J19: CONN_30; 1X30
J20, J21, J22, J23, J24, J25: CONN_03; 1X03
J38, J39, J40, J41: CONN_02; 1X02
J42: CONN_01; 1X01
LED13: E6CC1205RYGC2UDA; BICOLOR_LED
MIC: MICROPHONE
NTC: THERMISTOR; NTC
P1: SLIDE_POT_20MM; RS201111J011
P2, P3: ALPS_RK09K_VERTICAL
PH1: PHOTORESISTOR; GL5516
R38: 330; 0603
R67: 10k; 0603
S2, S3, S4, S5, S6, S7, S8, S9, S10: MOMENTARY-SWITCH-SPST-PTH-6.0MM; TACTILE_SWITCH_PTH_6.0MM
U1: ADXL335; LFCSP-16-4X4; LCSC C34439
U2: GAS_SENSOR
U$16: RESISTIVE_SENSOR_PAD

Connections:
5V: R38.2, U2.A1, U2.HA (H1); also elsewhere on the board
GND: C29.2, C30.2, C31.2, C32.2, J14.1, J14.2, J14.3, J14.4, J14.5, J14.6, J14.7, J14.8, J14.9, J14.10, J14.11, J14.12, J14.13, J14.14, J14.15, J14.16, J14.17, J14.18, J14.19, J14.20, J14.21, J14.22, J14.23, J14.24, J14.25, J14.26, J14.27, J14.28, J14.29, J14.30, LED13.1 (C), R67.1, U1.3 (COM), U1.5 (COM), U1.6 (COM), U1.7 (COM), U2.HB (H2); also elsewhere on the board
unnamed: J42.1, R67.2, U2.B1
unnamed: LED13.2 (A), R38.1
unnamed: J41.2, U$16.0
unnamed: J41.1, U$16.1
unnamed: J15.24, J16.24, J17.24, J18.24
unnamed: J15.30, J16.30, J17.30, J18.30
unnamed: J15.29, J16.29, J17.29, J18.29
unnamed: J15.28, J16.28, J17.28, J18.28
unnamed: J15.27, J16.27, J17.27, J18.27
unnamed: J15.26, J16.26, J17.26, J18.26
unnamed: J15.25, J16.25, J17.25, J18.25
unnamed: J15.23, J16.23, J17.23, J18.23
unnamed: J15.22, J16.22, J17.22, J18.22
unnamed: J15.21, J16.21, J17.21, J18.21
unnamed: J15.20, J16.20, J17.20, J18.20
unnamed: J15.19, J16.19, J17.19, J18.19
unnamed: J15.18, J16.18, J17.18, J18.18
unnamed: J15.17, J16.17, J17.17, J18.17
unnamed: J15.16, J16.16, J17.16, J18.16
unnamed: J15.15, J16.15, J17.15, J18.15
unnamed: J15.14, J16.14, J17.14, J18.14
unnamed: J15.13, J16.13, J17.13, J18.13
unnamed: J15.12, J16.12, J17.12, J18.12
unnamed: J15.11, J16.11, J17.11, J18.11
unnamed: J15.10, J16.10, J17.10, J18.10
unnamed: J15.9, J16.9, J17.9, J18.9
unnamed: J15.8, J16.8, J17.8, J18.8
unnamed: J15.7, J16.7, J17.7, J18.7
unnamed: J15.6, J16.6, J17.6, J18.6
unnamed: J15.5, J16.5, J17.5, J18.5
unnamed: J15.4, J16.4, J17.4, J18.4
unnamed: J15.3, J16.3, J17.3, J18.3
unnamed: J15.2, J16.2, J17.2, J18.2
unnamed: J15.1, J16.1, J17.1, J18.1
unnamed: J21.1, S2.3 (2), S5.3 (2), S8.3 (2)
unnamed: J21.2, S3.3 (2), S6.3 (2), S9.3 (2)
unnamed: J39.1, PH1.1
unnamed: J39.2, PH1.3
unnamed: J40.1, NTC.2
unnamed: J23.1, P2.3
unnamed: J23.2, P2.2
unnamed: J23.3, P2.1
unnamed: J22.1, P1.3
unnamed: J22.2, P1.2
unnamed: J22.3, P1.1
unnamed: J24.1, P3.3
unnamed: J24.2, P3.2
unnamed: J24.3, P3.1
unnamed: J38.1, MIC.2
unnamed: J38.2, MIC.1
unnamed: J20.3, S2.1, S3.1, S4.1
unnamed: J40.2, NTC.1
unnamed: J20.2, S5.1, S6.1, S7.1
unnamed: J21.3, S4.3 (2), S7.3 (2), S10.3 (2)
unnamed: J20.1, S8.1, S9.1, S10.1
VCC: C32.1, J19.1, J19.2, J19.3, J19.4, J19.5, J19.6, J19.7, J19.8, J19.9, J19.10, J19.11, J19.12, J19.13, J19.14, J19.15, J19.16, J19.17, J19.18, J19.19, J19.20, J19.21, J19.22, J19.23, J19.24, J19.25, J19.26, J19.27, J19.28, J19.29, J19.30, U1.14 (VS), U1.15 (VS); also elsewhere on the board
X+: C29.1, J25.1, U1.12 (XOUT)
Y+: C30.1, J25.2, U1.10 (YOUT)
Z+: C31.1, J25.3, U1.8 (ZOUT)

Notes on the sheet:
Pulsadores
Potenciómetros
Sensor táctil
Sensor de luz
Sensor de sonido
Sensor de temp
Sensor de aceleración
Bus bar
By JGAguado
Sensor de gas

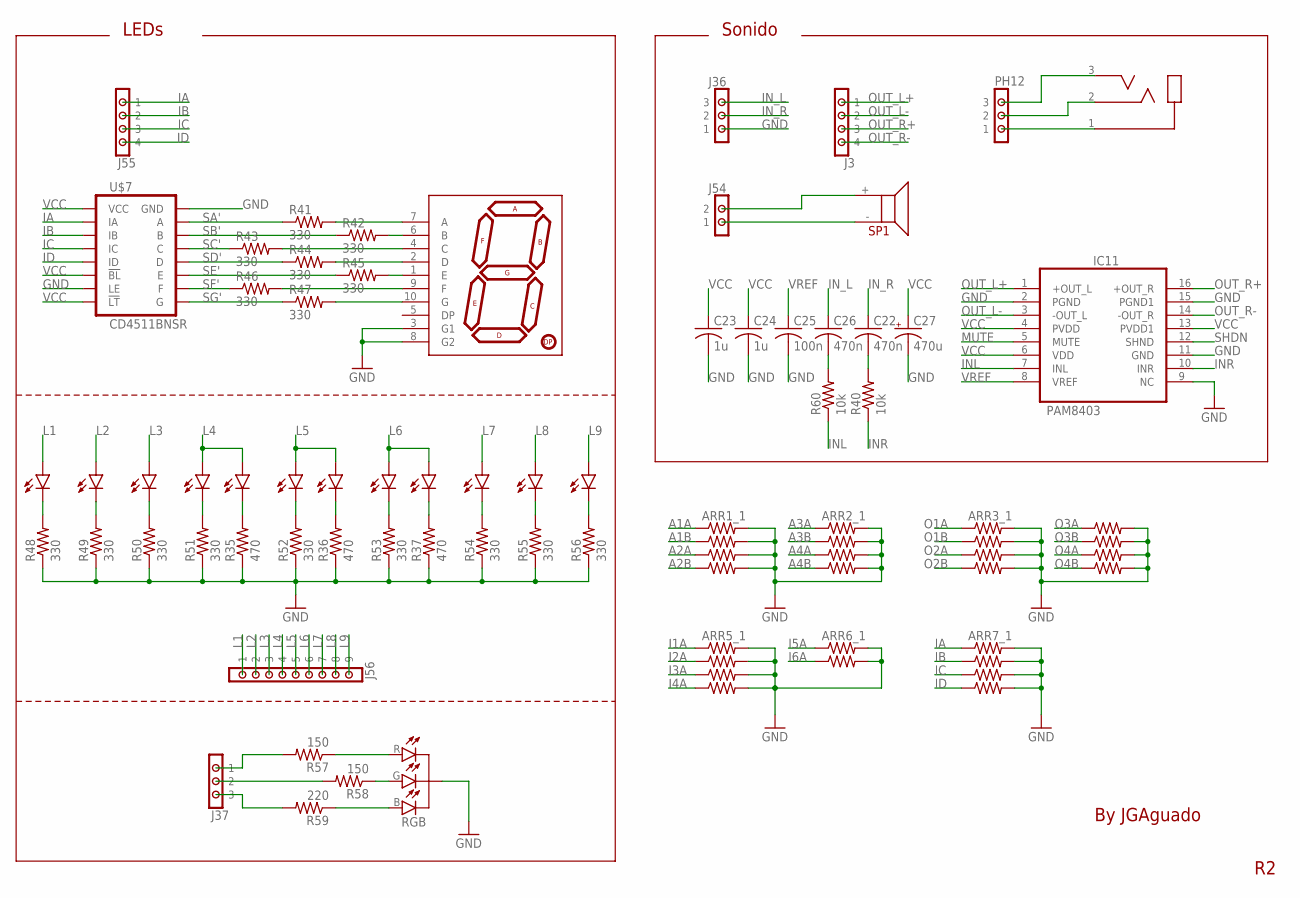
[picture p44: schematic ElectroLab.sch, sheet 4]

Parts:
ARR1, ARR2, ARR3, ARR4, ARR5, ARR6, ARR7: 4_RES_ARRAY_R06031KOHM; 0603-ARC
C22, C26: 470n; 0603
C23, C24: 1u; 0603
C25: 100n; 0603
C27: 470u; D/7343-31R; LCSC C7229
IC11: PAM8403; SOP-16
J3, J55: CONN_04; 1X04
J36, J37: CONN_03; 1X03
J54: CONN_02; 1X02
J56: CONN_09; 1X09
JACK: AUDIO_JACK_MONO_3.5_3P; HC-PJ-320A-3P-D
LED4, LED5, LED6, LED7, LED8, LED9, LED10, LED11, LED12: E6CC1205RYGC2UDA; BICOLOR_LED
PH12: CONN_03; 1X03
R35, R36, R37: 470; 0603
R40, R60: 10k; 0603
R41, R42, R43, R44, R45, R46, R47, R48, R49, R50, R51, R52, R53, R54, R55, R56: 330; 0603
R57, R58: 150; 0603
R59: 220; 0603
RGB: CLEAR; LED-RGB-THRU
SP1: SPEAKERFS1508MB0810-H8.0; FS1508MB0810-H8.0
U$1: FJ5101AG; 7-SEGMENT
U$7: CD4511BNSR; SO16

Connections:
A1A: ARR1.1; also elsewhere on the board
A1B: ARR1.2 (1); also elsewhere on the board
A2A: ARR1.3 (1); also elsewhere on the board
A2B: ARR1.4 (1); also elsewhere on the board
A3A: ARR2.1; also elsewhere on the board
A3B: ARR2.2 (1); also elsewhere on the board
A4A: ARR2.3 (1); also elsewhere on the board
A4B: ARR2.4 (1); also elsewhere on the board
B: J37.3, R59.2
G: J37.2, R58.2
GND: ARR1.5 (2), ARR1.6 (2), ARR1.7 (2), ARR1.8 (2), ARR2.5 (2), ARR2.6 (2), ARR2.7 (2), ARR2.8 (2), ARR3.5 (2), ARR3.6 (2), ARR3.7 (2), ARR3.8 (2), ARR4.5 (2), ARR4.6 (2), ARR4.7 (2), ARR4.8 (2), ARR5.5 (2), ARR5.6 (2), ARR5.7 (2), ARR5.8 (2), ARR6.7 (2), ARR6.8 (2), ARR7.5 (2), ARR7.6 (2), ARR7.7 (2), ARR7.8 (2), C23.2, C24.2, C25.2, C27.-, IC11.2 (PGND), IC11.9 (NC), IC11.11 (GND), IC11.15 (PGND1), J36.1, R35.1, R36.1, R37.1, R48.1, R49.1, R50.1, R51.1, R52.1, R53.1, R54.1, R55.1, R56.1, RGB.C, U$1.3 (G1), U$1.8 (G2), U$7.5 (LE), U$7.8 (GND); also elsewhere on the board
I1A: ARR5.1; also elsewhere on the board
I2A: ARR5.2 (1); also elsewhere on the board
I3A: ARR5.3 (1); also elsewhere on the board
I4A: ARR5.4 (1); also elsewhere on the board
I5A: ARR6.1; also elsewhere on the board
I6A: ARR6.2 (1); also elsewhere on the board
IA: ARR7.1, J55.1, U$7.7 (IA)
IB: ARR7.2 (1), J55.2, U$7.1 (IB)
IC: ARR7.3 (1), J55.3, U$7.2 (IC)
ID: ARR7.4 (1), J55.4, U$7.6 (ID)
INL: IC11.7 (INL), R60.1
INR: IC11.10 (INR), R40.1
IN_L: C26.1, J36.3
IN_R: C22.1, J36.2
L1: J56.1, LED4.2 (A)
L2: J56.2, LED5.2 (A)
L3: J56.3, LED6.2 (A)
L4: J56.4, LED7.2 (A), LED7.3 (A)
L5: J56.5, LED8.2 (A), LED8.3 (A)
L6: J56.6, LED9.2 (A), LED9.3 (A)
L7: J56.7, LED10.3 (A)
L8: J56.8, LED11.3 (A)
L9: J56.9, LED12.3 (A)
MUTE: IC11.5 (MUTE)
unnamed: JACK.2, PH12.2
unnamed: JACK.1, PH12.1
unnamed: R58.1, RGB.G
unnamed: LED4.1 (C), R48.2
unnamed: C26.2, R60.2
unnamed: C22.2, R40.2
unnamed: LED5.1 (C), R49.2
unnamed: LED6.1 (C), R50.2
unnamed: LED7.1 (C), R51.2
unnamed: LED8.1 (C), R52.2
unnamed: LED9.1 (C), R53.2
unnamed: LED7.4 (C), R35.2
unnamed: LED8.4 (C), R36.2
unnamed: LED9.4 (C), R37.2
unnamed: LED10.4 (C), R54.2
unnamed: LED11.4 (C), R55.2
unnamed: LED12.4 (C), R56.2
unnamed: J54.2, SP1.+
unnamed: JACK.3, PH12.3
unnamed: J54.1, SP1.-
unnamed: R57.1, RGB.R
unnamed: R59.1, RGB.B
O1A: ARR3.1; also elsewhere on the board
O1B: ARR3.2 (1); also elsewhere on the board
O2A: ARR3.3 (1); also elsewhere on the board
O2B: ARR3.4 (1); also elsewhere on the board
O3A: ARR4.1; also elsewhere on the board
O3B: ARR4.2 (1); also elsewhere on the board
O4A: ARR4.3 (1); also elsewhere on the board
O4B: ARR4.4 (1); also elsewhere on the board
OUT_L+: IC11.1 (+OUT_L), J3.1
OUT_L-: IC11.3 (-OUT_L), J3.2
OUT_R+: IC11.16 (+OUT_R), J3.3
OUT_R-: IC11.14 (-OUT_R), J3.4
R: J37.1, R57.2
SA: R41.2, U$1.7 (A)
SA': R41.1, U$7.13 (A)
SB: R42.2, U$1.6 (B)
SB': R42.1, U$7.12 (B)
SC: R43.2, U$1.4 (C)
SC': R43.1, U$7.11 (C)
SD: R44.2, U$1.2 (D)
SD': R44.1, U$7.10 (D)
SE: R45.2, U$1.1 (E)
SE': R45.1, U$7.9 (E)
SF: R46.2, U$1.9 (F)
SF': R46.1, U$7.15 (F)
SG: R47.2, U$1.10 (G)
SG': R47.1, U$7.14 (G)
SHDN: IC11.12 (SHND)
VCC: C23.1, C24.1, C27.+, IC11.4 (PVDD), IC11.6 (VDD), IC11.13 (PVDD1), U$7.3 (!LT), U$7.4 (!BL), U$7.16 (VCC); also elsewhere on the board
VREF: C25.1, IC11.8 (VREF)

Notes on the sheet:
Sonido
LEDs
By JGAguado

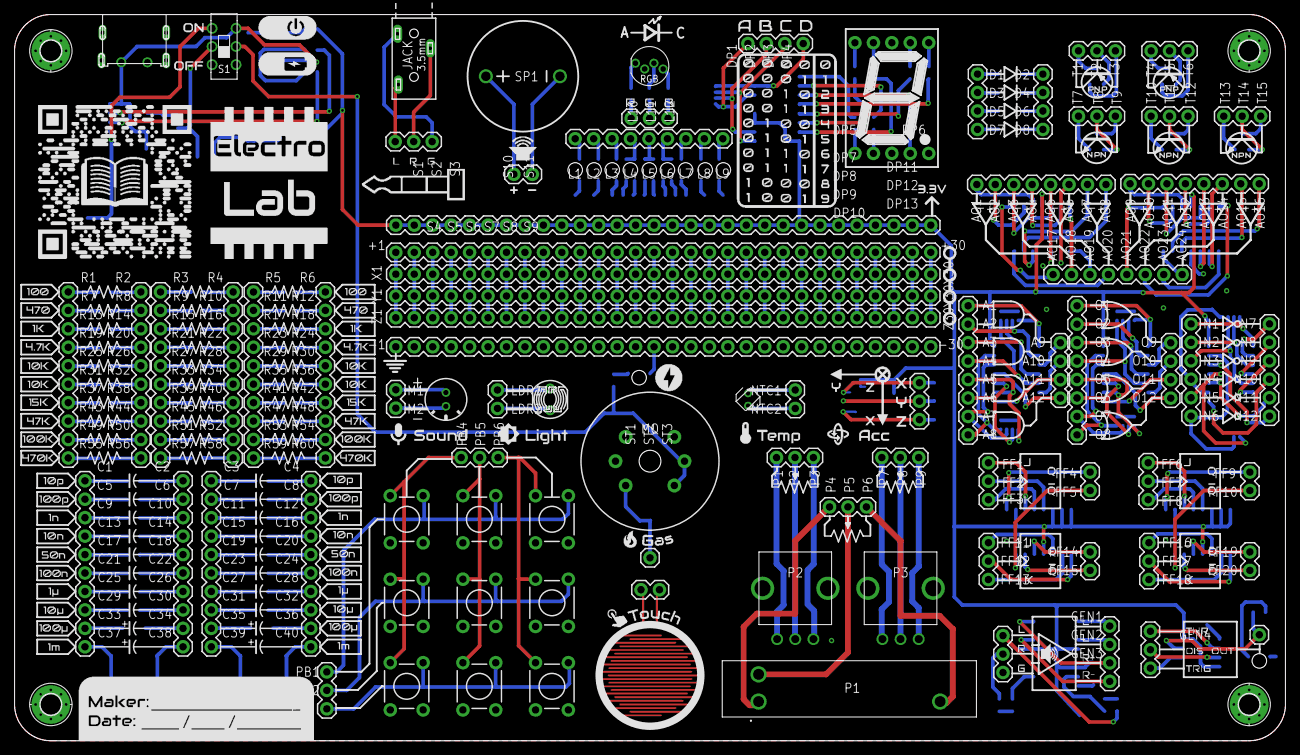
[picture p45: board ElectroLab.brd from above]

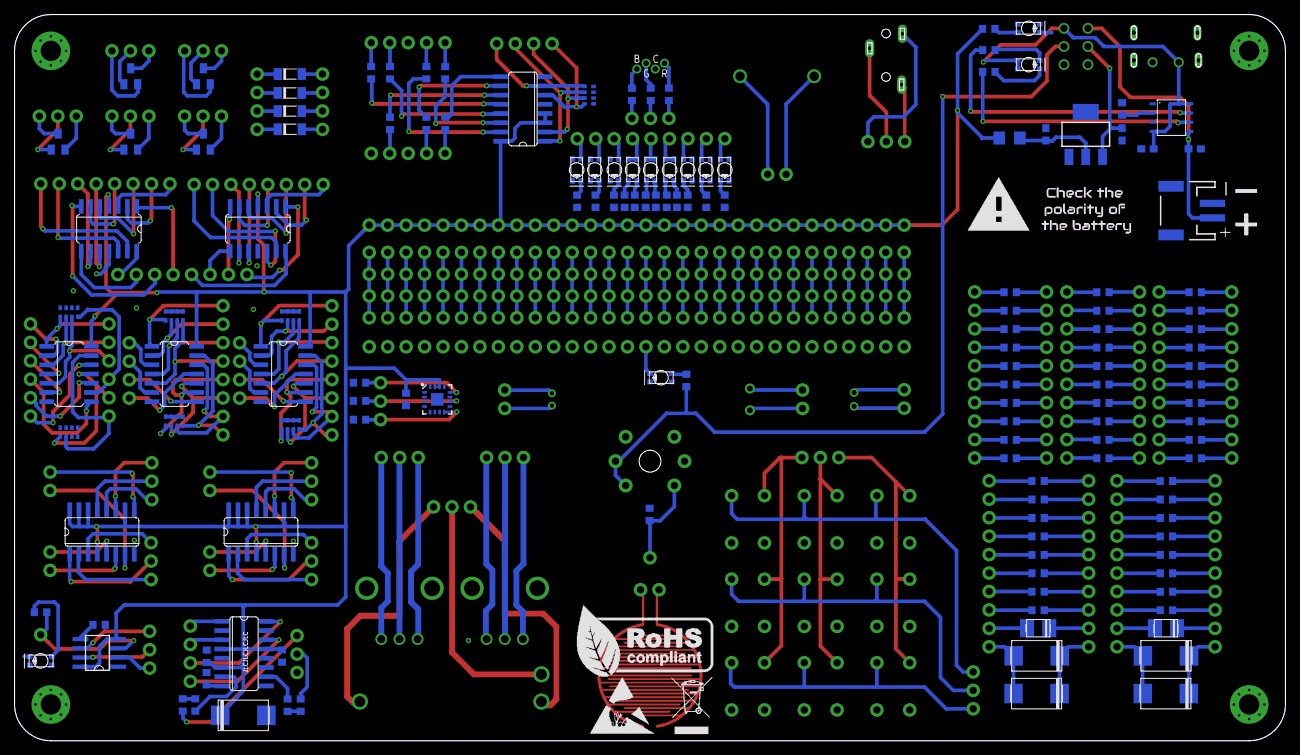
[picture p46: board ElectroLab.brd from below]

Board: 2 copper layers, 175.0 x 100.0 mm, 229 parts (142 on the bottom side), 341 nets.

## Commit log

2017-12-17 Initial Commit
    * Documentation: ElectroLab Top Layout
    * Hardware: SCH and BRD
    [ElectroLab R2.brd, ElectroLab R2.sch]
2019-01-22 IR sensor replaced with ADXL337 analog accelerometer. 5v to 3.3V power supply IC integrated. Analog level shift circuit based on Op. Amps 3.3v to 5V.
    [ElectroLab R2.sch]
2019-01-22 Analogic accelerometer ADXL337 Layout in BRD
    [ElectroLab R2.brd, ElectroLab R2.sch]
2019-01-22 Minor update of ADXL337 layout
    [ElectroLab R2.brd, ElectroLab R2.sch]
2019-01-22 Modified capacitive tactile sensor. Simplified design.
    [ElectroLab R2.brd, ElectroLab R2.sch]
2019-01-22 Mod: Seriegraphy and layout of ArduLab interface. Modified CTI related seriegraphy
    [ElectroLab R2.brd]
2020-01-22 Upgraded Electrolitic Capacitors to Tantalum Capacitors (C15-C18, C27)
    [ElectroLab R2.brd, ElectroLab R2.sch]
2020-01-23 Jumpers added to accelerometer outputs to optionally get the raw signal
    [ElectroLab R2.brd, ElectroLab R2.sch]
2020-01-23 Replaced Microphone footprint to fit with CMEJ-0627-42-P
    [ElectroLab R2.brd, ElectroLab R2.sch]
2020-01-23 Renamed the project ElectroLab
    [ElectroLab.brd, ElectroLab.sch]
2020-02-07 Removed Amplifier after Acc ADXL337
    [ElectroLab.brd, ElectroLab.sch]
2020-02-07 Updated RGB layout
    [ElectroLab.brd, ElectroLab.sch]
2020-02-28 Capacitor area update: - Replaced C19 & C20 for 470uF 7343 (2917) Tantalum capacitors - Added C35 & C36 470uF 7343 (2917) in paralel to C19 & C20 for making 940uF combined - Reviewed Name and Values 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
    [ElectroLab.brd, ElectroLab.sch]
2020-03-03 Updated board layout and silkscreen
    [ElectroLab.brd]
2020-04-08 Added Production files for R3V1_2
    [ElectroLab_R3V1_2_Centroid.csv, ElectroLab_R3V1_BOM.csv, copper_bottom.gbr, copper_top.gbr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]
2020-05-10 Update modifications for ElectroLab R2 CTI20 Release
    [ElectroLab.brd, ElectroLab.sch]
2020-05-24 Updated BRD with manufactured silkscreen R2
    [ElectroLab.brd]
2021-04-05 First R3 version before merging silkscreen layers
    [ElectroLab.brd, ElectroLab.sch]
2021-05-02 Updated to R3 (Mk.III)
    [ElectroLab.brd, ElectroLab.sch]
2021-05-02 Updated: * Documentation * Silkscreens
    [drills.xln]
2021-05-02 Updated Documentation/Top.png with values for resistors & capacitors
2022-04-15 Updated structure
    [ElectroLab.brd, ElectroLab.sch]
2023-08-12 Updated V3R1
    [ElectroLab.brd, ElectroLab.sch]
2023-08-13 Added circuits
2023-08-15 HTML Circuit generator
2023-08-16 V3 fixed: - USB-C - BCD pinhead - 330 -> 470 Ohm on RED LEDs for orange led bards
    [ElectroLab.brd, ElectroLab.sch]
2023-08-27 Replaced Jack connector MQ-2 sensor power through main switch
    [ElectroLab.brd, ElectroLab.sch]
2023-08-27 Set & reset connected to VCC (3.3V) instead of GND
    [ElectroLab.brd, ElectroLab.sch]
2023-09-26 Added design files
    [ElectroLab.brd, ElectroLab.sch]

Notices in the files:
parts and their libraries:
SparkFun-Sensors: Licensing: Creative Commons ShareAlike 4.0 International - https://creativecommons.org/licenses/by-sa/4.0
